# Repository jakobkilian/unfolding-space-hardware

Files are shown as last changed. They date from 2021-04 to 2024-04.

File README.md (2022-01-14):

# Unfolding Space Hardware

This repo contains the **hardware documentation of the “Unfolding Space” glove** – a prototypical open source navigation aid system for the visually impaired. 

Please check out the main repository of the [Unfolding Space](https://www.github.com/jakobkilian/unfolding-space) project for more information and a list of related repos anc content.

## Overall structure

In order to be able to use the Unfolding Space Glove, a relatively large amount of custom work is necessary. The following readme is only intended to give an overview of this and the contents of this repo. Note that not all details or design decisions are not documented here - if you really plan to build your own model, feel free to contact me if you have any questions.

The overall structure consists of 3 components:

- **5V USB power bank:** You can basically use any and wear it wherever you want. To keep the cable out of the way, I attached it to the upper arm with a sports arm band. I was using:
  - [Hama Power Pack *Supreme 10HD*](https://hama.com/00188307/hama-power-pack-supreme-10hd-10000mah). Raspis are picky about the supply voltage – if it drops too low (I think below 4.8 V), they reboot. Since they consume up to 3 A, the voltage of many batteries can easily drop below 5.0 V at peaks. Use high-quality power packs and 10 Ah to avoid this in advance or find one having stable output with > 4.9 V.
  - [SP Connect Running Band](https://sp-connect.com/collections/mounts/products/running-band) and a adhesive [Universal Interface](https://sp-connect.com/collections/phone-cases/products/universal-interface) was used to mount the power bank to the upper arm. Expensive but very reliable for this use case. There is tons of other, cheaper options out there.
- **USB-C Cable:** Here too, maintaining the voltage is crucial: use the shortest possible cable with good quality. The thickness of the insulation is a good indicator for low voltage drop, but only cutting and testing the copper wires can provide certainty. I had a 30 cm USB-A to USB-C cable from *Renkforce* in use (pictured), there may be plenty of others in your country.
- An finally **a) The Glove** hosting vibration motors and **b) the Unfolding Space Carrier Board** hosting the Raspberry Pi. See next sections.

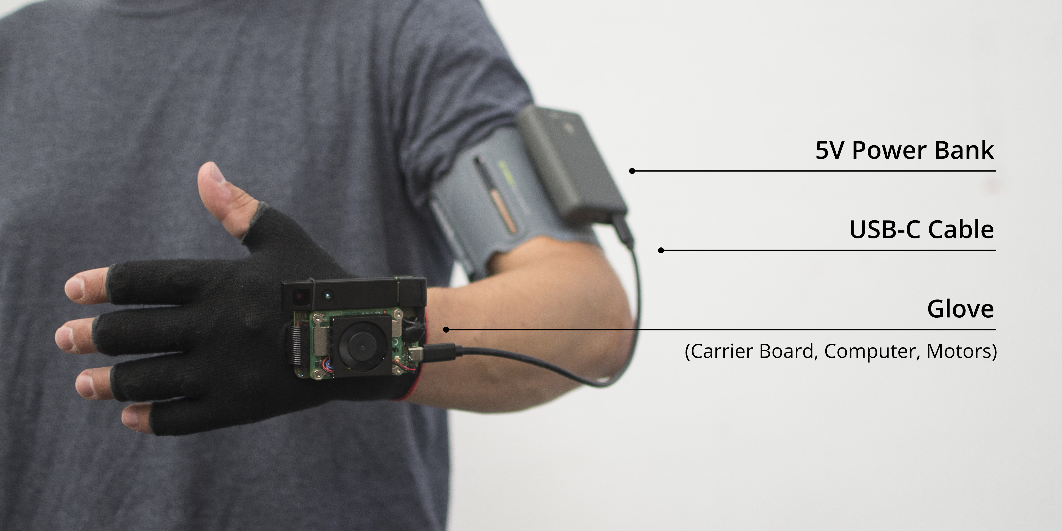
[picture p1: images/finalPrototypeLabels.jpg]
Prototype with labels


### a) The Glove

The glove consists of two textile layers between which the motors are attached and the cables are laid. On the outside (back of the hand) there are Velcro fasteners and an IDC connector for attaching the carrier board. Currently there are two sizes, fitting most hand shapes and sizes. The production of the glove is relatively elaborate and is explained step by step in the [glove](glove) directory of this repo.

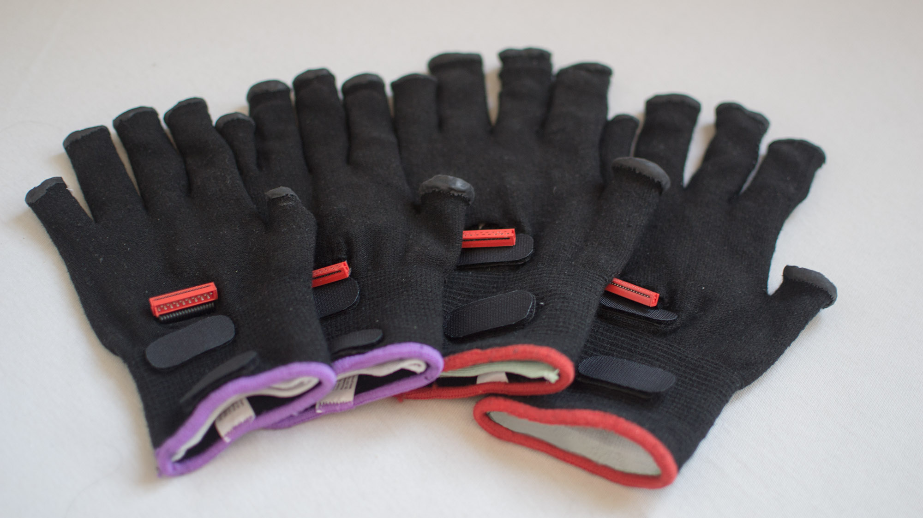
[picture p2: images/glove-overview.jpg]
Glove Overview


### b) Unfolding Space Carrier Board

The carrier board again consists of multiple components:

- The **Glove Connector** is implemented via an IDC connector soldered onto the PCB. *See [pcb](pcb)  directory for details and instructions.*
- The **ToF Camera** (a [Pico Flexx](https://pmdtec.com/picofamily/) camera from pmdtechnologies) is attached with a rubber band and a USB 3.0 Micro-B connector (originally this was a short cable), which is glued to the PCB. *See [pcb](pcb)  directory for details and instructions.*
- The **Raspberry Pi Compute Module 4** ([Link](https://www.raspberrypi.com/products/compute-module-4)) which serves as a computing unit. I used the CM4101016 configuration (16 GB Flash, 1 GB RAM, Wifi), a cheaper one (if available) would also do it as the app doesnt need much RAM.
- A **Cooling Fan for the CM4** was necessary because it became uncomfortably hot on warm days and passive cooling alone was not sufficient. At 24°C room temperature, the core temperature rose to >75°C without cooling, to ~67° with a small heat sink ([link](https://www.waveshare.com/cm4-heatsink.htm)) and to ~59°C with a larger one ([link](https://geekworm.com/products/cm4-12mm-aluminum-alloy-heatsink-c235?variant=33569307394136)). If you add a cooler to the latter ([link](https://geekworm.com/products/cm4-12mm-aluminum-alloy-heatsink-c235?variant=33569307426904)) or use [this smaller fan](https://www.waveshare.com/cm4-fan-3007.htm) (pictured) , it stays below 45°C. The last fan from Waveshare used in the picture operates with 12V and PWM. However, I used it without PWM and with 5V, which made it run very quietly.
- And then there is the **custom made PCB ** that carries the CM4 with two 100-pin mezzanine connectors, hosts the motors drivers, some electronics (gyro, compass, ...), the 5V USB-C power supply plug, the IDC connector to the glove and the USB connector to the ToF camera. ***See [pcb](pcb) directory for details and instructions.***

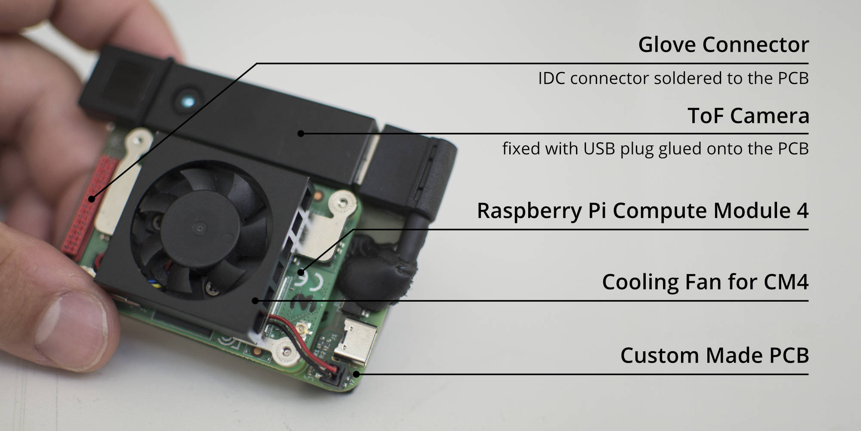
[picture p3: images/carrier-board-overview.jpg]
Carrier Board Overview


## Parts and Prices

There is a parts list / BOM with all components assembled on the root directory (called [bom-overall](bom-overall.csv)) which refers to further BOMs in directories [pcb](pcb) and [glove](glove). The total price of the overall structure is about $ 500, two thirds of which go to the ToF camera. Take a look at the BOMS for details.

## 3D Design

I did some 3D designs to check wheter the parts will fit and to dtermine size of the board etc. You can find them under [3D-design](3D-design), but note that they are not the final version (e.g. the cooling fan is not included) and they are for orientation only.

## Credits

Thanks to **[mattikra](https://github.com/mattikra)** and **[a2800276](https://github.com/a2800276)** from Press Every Key for helping me with the PCB design and ordering of the boards and parts!

Thanks to [dronecz](https://github.com/dronecz/Minimal_carrier_board_for_CM4)  and [timonsku](https://github.com/timonsku/Minimal-RPi-CM-4-Carrier) for some carrier board inspiration just after the CM4s were released.

Thanks to Shawn Hymel for providing a [tutorial on CM4 carrier boards](https://www.digikey.com/en/maker/projects/creating-a-raspberry-pi-compute-module-4-cm4-carrier-board-in-kicad/7812da347e5e409aa28d59ea2aaea490) and an exemplary KiCad template file (included in [pcb](pcb) , licensed under CC-BY-4.0)

Thanks to KiCad for providing Software and [Libraries](https://gitlab.com/kicad/libraries) for this project.

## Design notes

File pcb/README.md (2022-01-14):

# Custom PCB: Unfolding Space Carrier Board Rev. 2

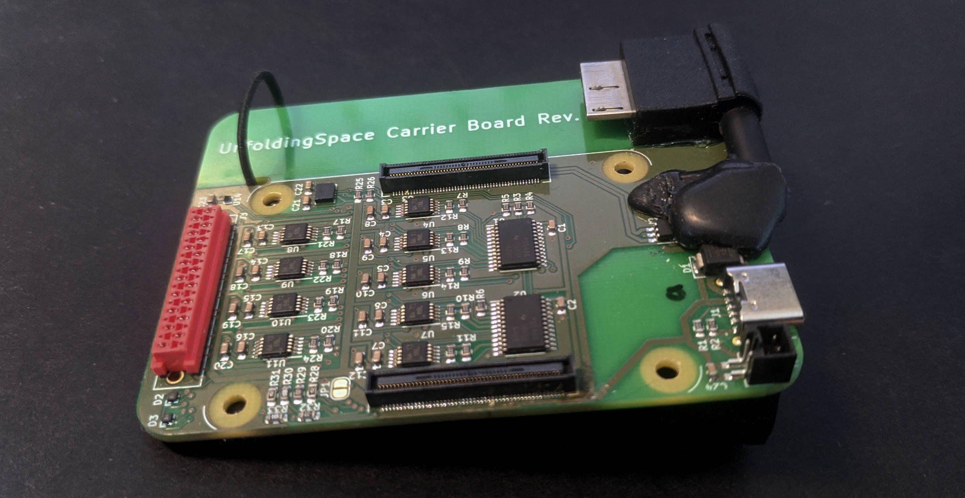
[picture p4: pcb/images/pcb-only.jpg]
The printed circuit board without Raspberry Pi and camera


## PCB Design Files

You can find the **design files** in [KiCad-Project-Rev2](KiCad-Project-Rev2) and exports (**schematic, pcb layout, rendering**) in [exports](exports).

**Design rules** are based on the specifications of a *2-layer, complex, ENIG* board at aisler.net. Note that some of my rules thus are a bit unusual (e.g. clearance ≥ 0.1 mm or track width ≥ 0.2 mm; through whole ≥ 0.3mm). [See all specifications of Aisler here.](https://aisler.net/help/design-rules-and-specifications/design-rules) 

There also is a [Aisler project of the Rev. 2 board online](https://aisler.net/p/WSTOTZAR) if you are from Europe. Attention: the BOM / parts list needs to be updated to respective components by hand!

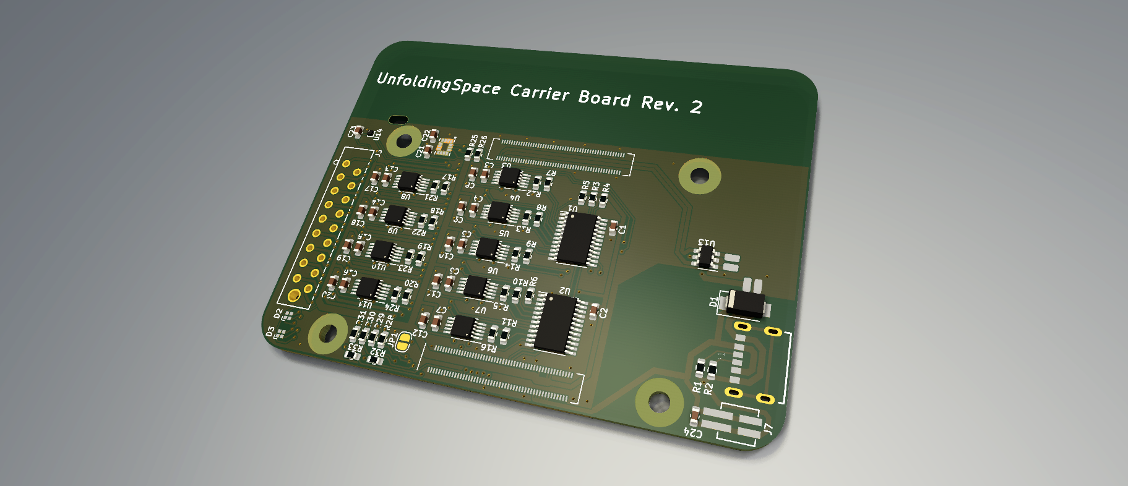
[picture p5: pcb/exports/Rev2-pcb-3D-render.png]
unfolding2


## BOM / parts list

See [bom-pcb](bom-pcb.csv) for a list with all needed parts for the pcb alone.

## Known issues

- Some parts (e.g. RGB LEDs, IMU and MMC) are very (very) small! We could successfully reflow them but it was quite a hustle.
- The RGB LEDs in the upper right corner are very bright in the current layout. We thus use GPIO pins of the raspi with pull-up resistor to drive them on lower light intensity. Consider changing the resistors on the board!
- The i2c multiplexer (PCA) is needed because the drv chips just have one i2c address. You could also use the drv2603 and use pwm to drive them. Writing on all 9 drvs with the multiplexer takes around 3ms. Not much time to save anyway...
- Shortly before dispatch, the pico-spox plug in the bottom left corner was added to drive a cooling fan with 5 V. Consider using a 4-pin plug and using pwm instead.

## Credits

Thanks to **[mattikra](https://github.com/mattikra)** and **[a2800276](https://github.com/a2800276)** from Press Every Key for helping me with the PCB design and ordering of the boards and parts!

Note the txt files in the directories of 3rd party assets for credits and licenses.

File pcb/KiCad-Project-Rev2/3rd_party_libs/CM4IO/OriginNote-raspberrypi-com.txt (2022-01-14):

Note that this library is taken from https://github.com/ShawnHymel/rpi-cm4-base-carrier, licensed under CC-BY-4.0. 

The CM4IO library is also availabe at https://www.raspberrypi.com/products/compute-module-4-io-board/

If you want to use the file(s) in your own project, consider downloading it yourself.

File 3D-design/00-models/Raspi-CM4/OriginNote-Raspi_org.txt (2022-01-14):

Note that this asset is taken from https://datasheets.raspberrypi.com

There it says:
_______________
All design files are made available openly, with no limitations. Files hosted on this site and under this licence include,
cm4/CM4-step.zip

Permission to use, copy, modify, and/or distribute this design for any purpose with or without fee is hereby granted.

THE DESIGN IS PROVIDED "AS IS" AND THE AUTHOR DISCLAIMS ALL WARRANTIES WITH REGARD TO THIS DESIGN INCLUDING ALL IMPLIED WARRANTIES OF MERCHANTABILITY AND FITNESS. IN NO EVENT SHALL THE AUTHOR BE LIABLE FOR ANY SPECIAL, DIRECT, INDIRECT, OR CONSEQUENTIAL DAMAGES OR ANY DAMAGES WHATSOEVER RESULTING FROM LOSS OF USE, DATA OR PROFITS, WHETHER IN AN ACTION OF CONTRACT, NEGLIGENCE OR OTHER TORTIOUS ACTION, ARISING OUT OF OR IN CONNECTION WITH THE USE OR PERFORMANCE OF THIS DESIGN.

The models provided in the 3dmodels directory as part of the CM4 design files are from various manufacturers including; Diodes, MTCONN, Toby, TRXCOM. Terms and conditions for the use of the models remain with the original manufacture.

also see: https://datasheets.raspberrypi.com/licence.html

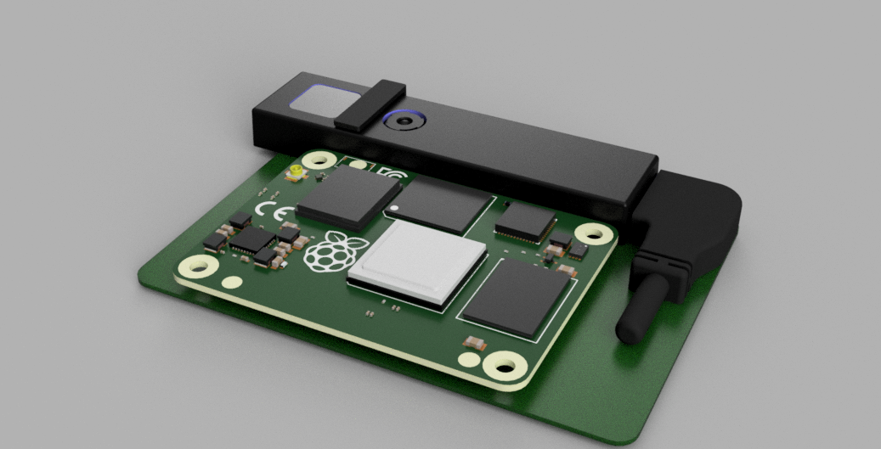
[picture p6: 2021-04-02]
3D-design/02-exports/210402_export.png

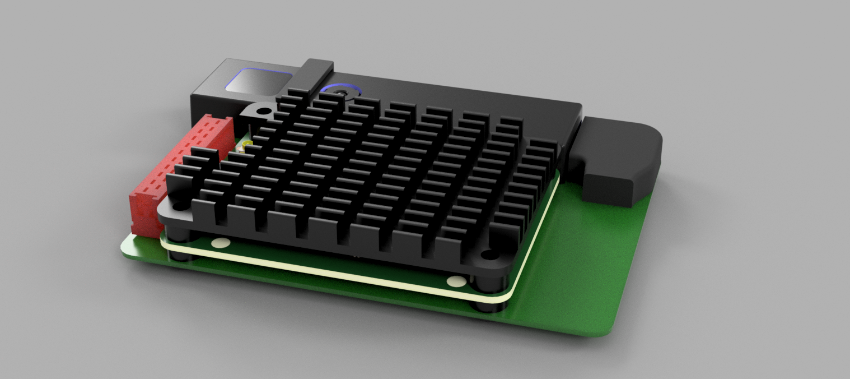
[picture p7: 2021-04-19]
3D-design/02-exports/200412_export_2.png

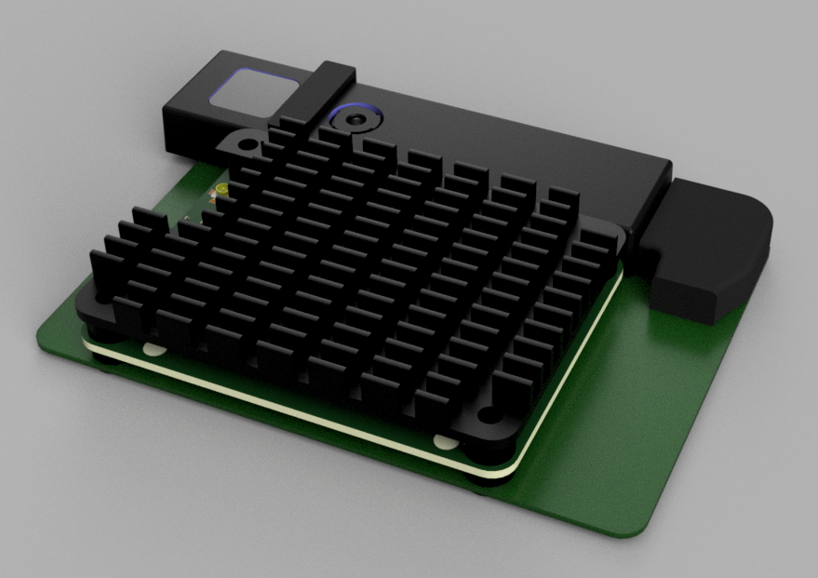
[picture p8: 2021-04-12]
3D-design/02-exports/210412_export.png

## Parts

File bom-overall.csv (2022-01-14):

Id | Designator | Manufacturer | Quantity | Designation | Description | Est. Price EUR | Link
1 | pcb |  | 1 |  | see pcb bom for details | 66 | pcb/bom-pcb.csv
2 | glove |  | 1 |  | see glove bom for details | 47 | glove/bom-glove.csv
3 | Raspberry Pi Compute Module 4 | Raspberry Pi Foundation | 1 | CM4101016 | CM4101008 would also suffice | 40
 | Cooling Fan for the CM4 | Waveshare | 1 | cm4-fan-3007 |  | 9 | https://www.waveshare.com/cm4-fan-3007.htm
 | ToF Camera | pmdtechnologies ag | 1 | CamBoard Pico Flexx | version 2 released in Jan 2022 | 300 | https://www.automation24.co.uk/development-kit-pmd-vision-r-camboard-pico-flexx-700-000-094
 | USB-C Cable | Renkforce | 1 | RF-3241262 | short USB-C cablecould be anyÉ | 7
 | 5V USB power bank | Hama | 1 | 188307 | 10 Ah Power Bank, could be anyÉ | 20
 |  |  |  |  | SUM | 489

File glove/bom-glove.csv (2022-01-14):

Id | Designator | Manufacturer | Quantity | Designation | Description | Est. Price EUR | Link
s | inner glove layer | Munitec GmbH | 1 | 12025 | clean room glove made of polyamide | 1 | https://www.munitec-gmbh.de/polyamid-reinraum-handschuhe-glatt.html
2 | outer glove layer | Worksave | 1 | L71-720 | see glove bom for details | 1
3 | sock stop liquid latex |  | 1 |  | Available in any craft shop or online | 2
4 | wooden stick 19mm |  | 1 |  | Available in any craft shop or online | 1
5 | Flat ribbon cable | 3M | 1 | 8125/10 100 | grey cable, found a black one in a local shop | 2 | https://www.digikey.de/short/fwfd03w9
6 | IDC Connector | TE Connectivity | 1 | 8-215083-8 | idc connector to join pcb and glove | 7 | https://www.digikey.de/short/3zfqqqv3
7 | Vibration Motors | Jinlong Machinery & Electronics | 1 | G1040003D | Strong LRA vibration motors. They seem to have changed their Designation to: VG1040003D Ð Vybronics, Inc | 29 | https://www.digikey.de/short/zwzpjh5d
8 | heat shrink tube |  | 1 |  | availbe in any electronics store or online | 1
9 | velcros |  | 4 |  | Available in any craft shop or online | 2
10 | motor adhesive surface | 3M | 1 | 3M241471 | needed to glue textile and shrink tube | 1 | https://www.3m.co.uk/3M/en_GB/p/d/v000090527/
 |  |  |  |  | SUM | 47

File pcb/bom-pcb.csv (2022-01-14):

Id | Designator | Package | Quantity | Designation | Description | Est. Price EUR | Link
1 | J3 | https://www.digikey.de/de/products/detail/te-connectivity-amp-connectors/8-215083-8/1955684 | 1 | 1-338068-8 | IDC socket for glove connection | 1.5
2 | C19;C15;C10;C13;C9;C5;C16;C14;C12;C24;C4;C2;C1;C3;C8;C20;C17;C18;C11;C6;C7 | C_0603_1608Metric | 21 | 1u | capacitor | 1
3 | C21;C22 | C_0603_1608Metric | 2 | 100n | capacitor | 0
4 | C23 | C_0603_1608Metric | 1 | 2.2u | capacitor | 0
5 | D1 | D_SMA | 1 | SMBJ5.0A | ESD for USB-C power supply | 0.5
6 | J1 | GCT_USB4125-GF-A_REVA | 1 | USB4125-GF-A_REVA | USB-C power supply socket | 0.5
7 | ToFCam-Stecker | Micro-USB30-Plug | 1 | System-S USB 3.0 cable | glued USB plug | 9 | https://www.system-s.com/USB-3-0-Micro-B/SYSTEM-S-Micro-USB-3-0-Kabel-90-GRAD-Grad-Winkel-Rechts-gewinkelt-auf-USB-Typ-A-3-0-Aufwaerts-gewinkelt-Adapter-Daten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
8 | J7 | PICOspox-2-v | 1 | PICOspox-2-v | cooling fan plug | 0.5
9 | U12 | PQFN50P250X300X100-14N | 1 | LSM6DSxx | IMU / Accelerometer and Gyroscope | 5
10 | R28;R31 | R_0603_1608Metric | 2 | 1K | resistor | 0
11 | R18;R19;R17;R7;R11;R13;R16;R3;R20;R9;R22;R26;R15;R24;R10;R25;R12;R4;R23;R8;R14;R21 | R_0603_1608Metric | 22 | 2K2 | resistor | 1
12 | R29;R32 | R_0603_1608Metric | 2 | 220 | resistor | 0
13 | R33;R30 | R_0603_1608Metric | 2 | 150 | resistor | 0
14 | R6;R5 | R_0603_1608Metric | 2 | 10K | resistor | 0
15 | R1;R2 | R_0603_1608Metric | 2 | 5K1 | resistor | 0
19 | U13 | SOT-23-6 | 1 | WE 82400102 | TVS diode for USB data (camera) | 1
20 | U2;U1 | TSSOP-24_4.4x7.8mm_P0.65mm | 2 | TCA9548APWR | i2c multiplexer | 7
21 | D3;D2 | UHD1110-FKA | 2 | UHD1110-FKA | RGB LED | 0.5
22 | U3;U5;U10;U8;U4;U11;U9;U7;U6 | VSSOP-10_3x3mm_P0.5mm | 9 | DRV2605LDGS | motor driver | 33
23 | U14 | WLP-4_0.86x0.86mm_P0.4mm | 1 | MMC5633NJL | compass | 1.5
24 | - |  | 2 | DF40HC(3.0)-100DS-0.4V(51 | 100pin mezzanine connector for CM4 | 4 | https://www.mouser.de/ProductDetail/Hirose-Connector/DF40HC30-100DS-04V51?qs=%252BAZVS4b%2FkgIV%252B3vHYy2dCA%3D%3D
25 | - |  | 1 |  | Board production | 10
 |  |  |  |  | SUM | 76

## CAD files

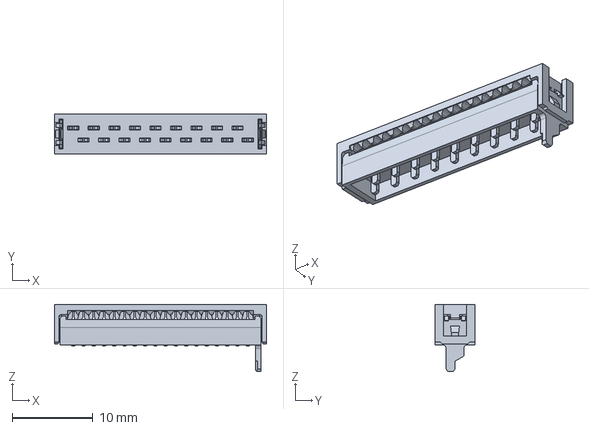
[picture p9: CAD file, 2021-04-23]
3D-design/00-models/TE-Connectors/c-1-215083-8-u-3d.stp
26.2 x 5.00 x 8.35 mm

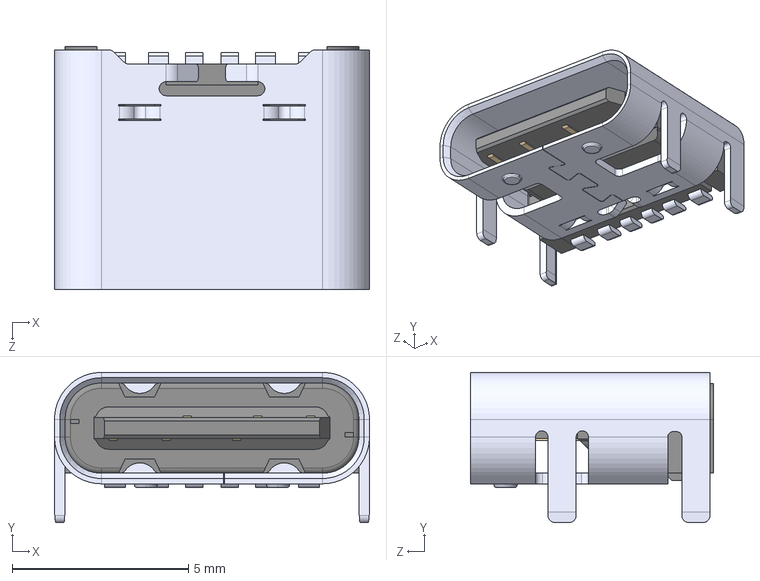
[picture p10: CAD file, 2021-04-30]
pcb/KiCad-Project-Rev2/3rd_party_libs/UJC-HP-3-SMT-TR/UJC-HP-3-SMT-TR.step
8.94 x 4.26 x 6.90 mm

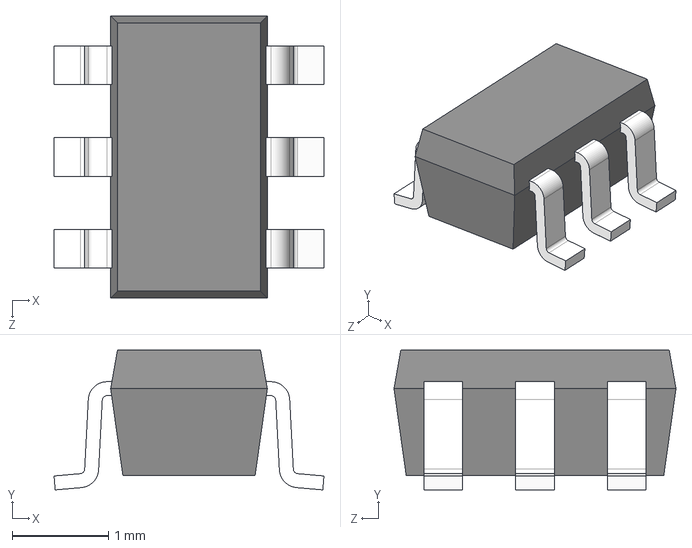
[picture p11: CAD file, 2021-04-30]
pcb/KiCad-Project-Rev2/3rd_party_libs/USBLC6-2SC6/USBLC6-2SC6.step
2.80 x 1.45 x 2.92 mm

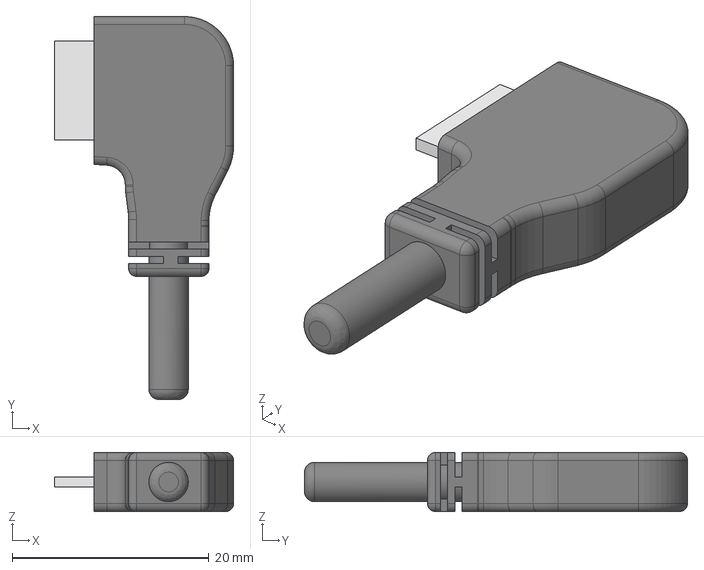
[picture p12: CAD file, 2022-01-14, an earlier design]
3D-design/00-models/USB-plug-deprecated/startech-plug.step
18.2 x 38.9 x 6.00 mm

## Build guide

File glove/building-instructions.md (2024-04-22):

# Building the Glove

This is a building instruction for the glove needed to build the the [Unfolding Space Glove](https://github.com/jakobkilian/unfolding-space).

## Overview

The glove has two layers of fabric with the vibration motors and cables in between. There is velcro to attach the Unfolding Space Carrier Board (see pcb directory of this repo) to it and a ribbon cable exiting the back of the glove terminating with an idc connector to link glove and board. The end result looks like this (two sizes: red = big and purple = small): 

The glove when it is finished. There are two sizes: red = big and purple = small

## 1. Textile Work

First of all, we need the inner and outer layers of the glove. You could sew these yourself, but this is very time-consuming. I therefore looked for suitable models which I could work with. It quickly became clear that both gloves had to be very thin, because otherwise the construction would be too thick and uncomfortable. In order to achieve a high degree of stretch and durability at the same time, I looked primarily for polyamide textiles. Most of them are work gloves with coating, which made the search more difficult.

I found what I was looking for in a very thin inner layer of a polyamide [clean room glove ](https://www.munitec-gmbh.de/polyamid-reinraum-handschuhe-glatt.html)(article number 12025) from Munitec (they were kind enough to provide me with samples of their collection). They can also be cut well without becoming frayed.

The outer layer should meet basic aesthetic requirements, look neutral and also be stretchable and resistant. Here it was a no name (Worksafe L71-720) product from Amazon (though I hate buying there).

### Outer Layer

I cut the fingers of the gloves halfway so that the two sizes would fit as well as possible on different hands. 

| Cut the Fingers Halfway                                                                                              |
|:--------------------------------------------------------------------------------------------------------------------:|
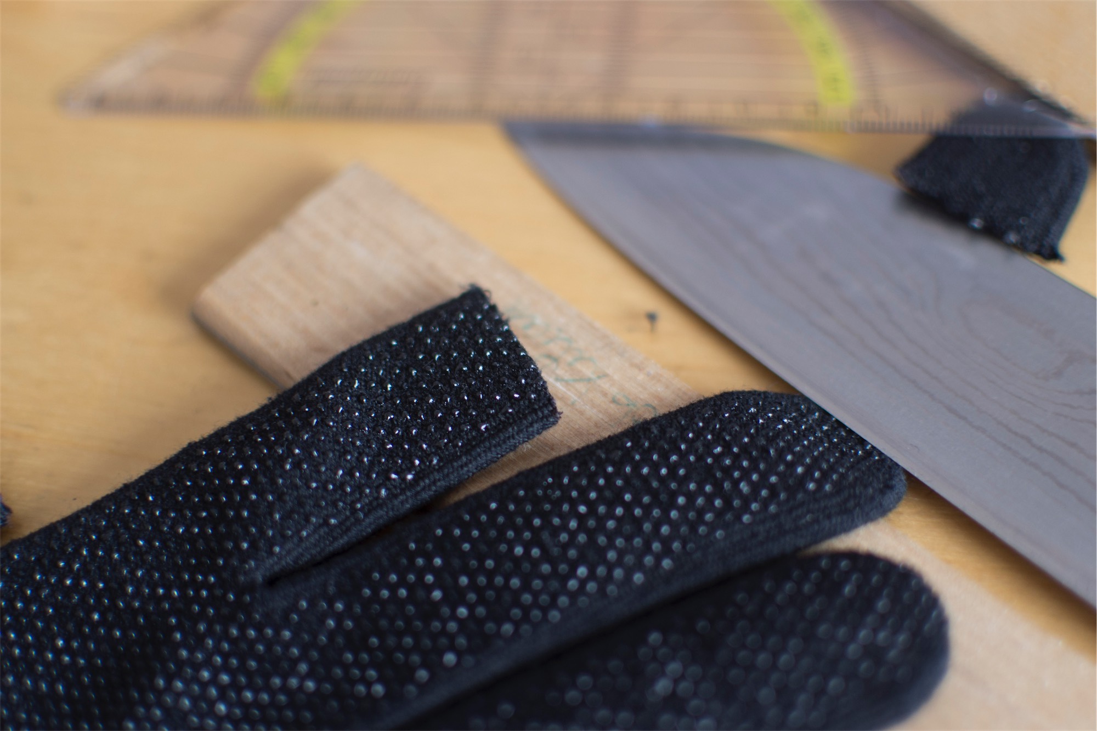
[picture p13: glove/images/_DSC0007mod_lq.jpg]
A kitchen knife next to the cut-in-half finger of the black glove on a wooden surface.
|  |
| To avoid fraying in the first place, it proved most effective to use a sharp kitchen knife                           |

Since I don't have a tool to hem the cut edges of the fingers (no idea how that would work), I experimented a bit with anti-fraying glue and the like and finally settled on liquid latex, typically used to make anti-slip socks. With some wooden stuffing of the fingers I was able to dip them into the latex and cut a clean edge after drying:

| Stuffing Material                                                                       | Just Before Dipping                                                                                                 |
|:---------------------------------------------------------------------------------------:|:-------------------------------------------------------------------------------------------------------------------:|
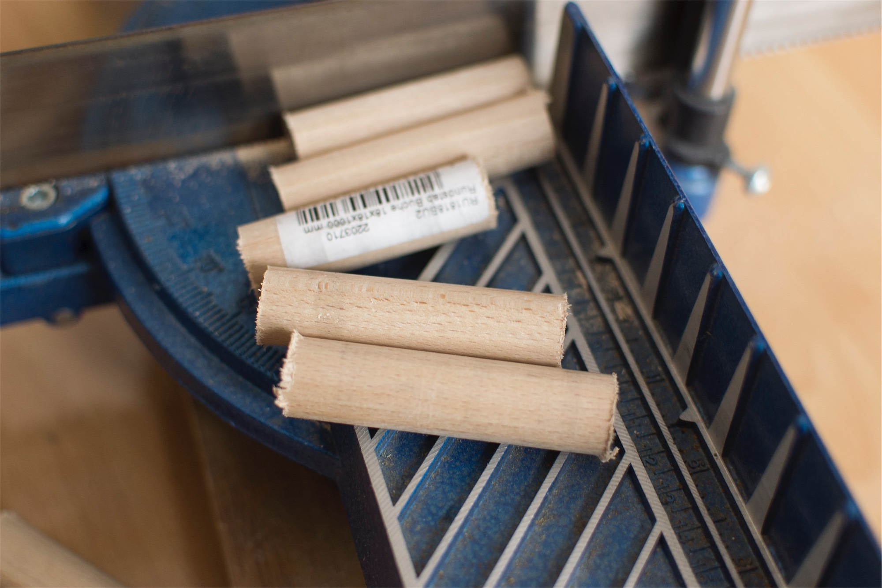
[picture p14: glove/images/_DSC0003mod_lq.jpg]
Short pieces of a wooden stick used as stuffing material.
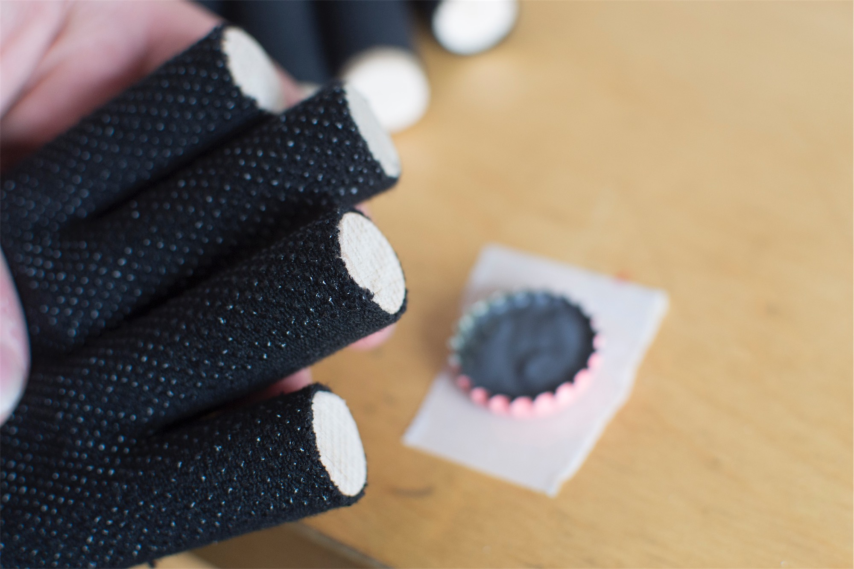
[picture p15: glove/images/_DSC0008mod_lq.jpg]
The fingers of the glove stuffed with the pieces of wooden stick just before dipping.
|  |  |

| After Dipping                                                                                           | Drying...                                                                          |
|:-------------------------------------------------------------------------------------------------------:|:----------------------------------------------------------------------------------:|
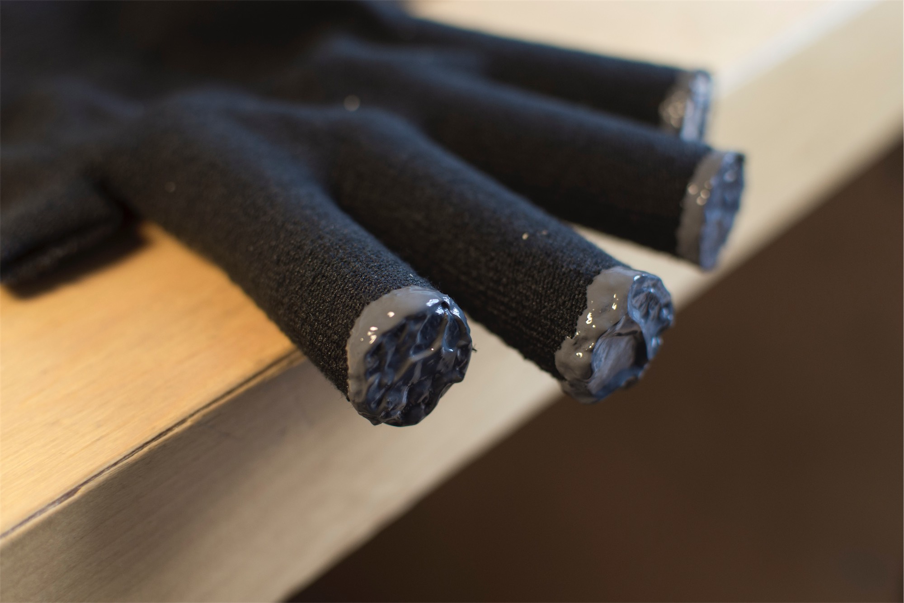
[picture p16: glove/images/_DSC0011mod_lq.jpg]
Fresh, grey liquid latex at the fingertips of the glove after dipping it.
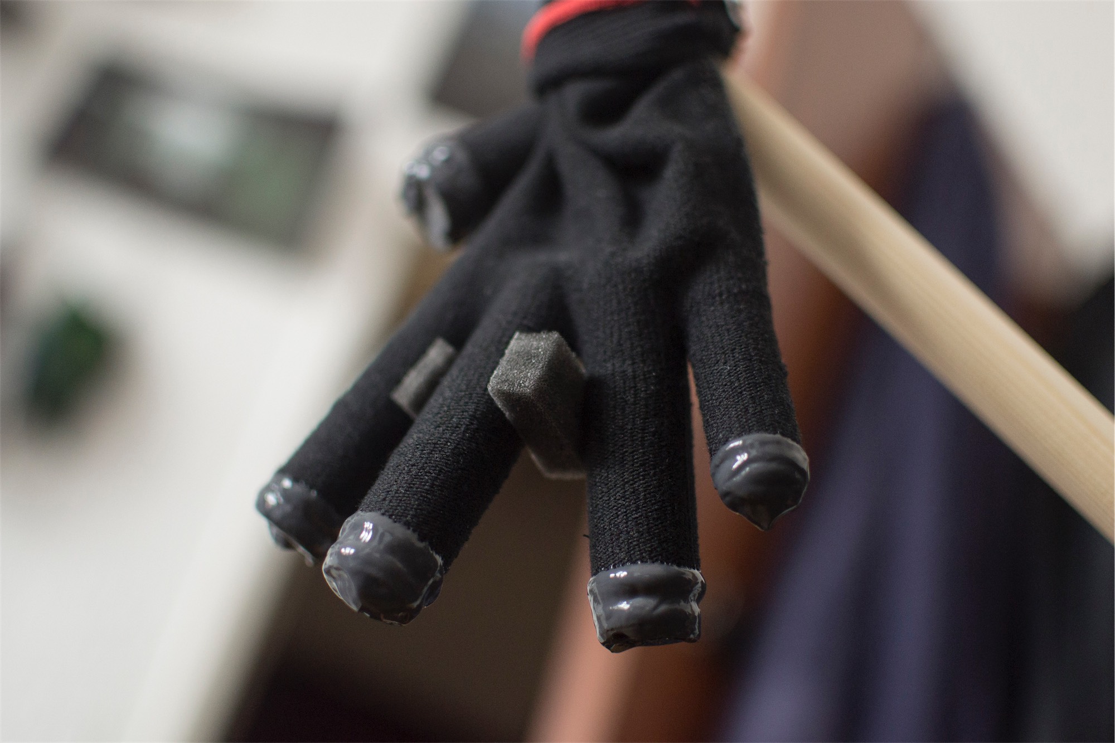
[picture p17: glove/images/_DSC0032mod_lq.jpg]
Suspended glove with drying latex on the fingertips.
|  |  |

| Getting Rid of Overhang                                                       | Finish Edges                                                                                                                |
|:-----------------------------------------------------------------------------:|:---------------------------------------------------------------------------------------------------------------------------:|
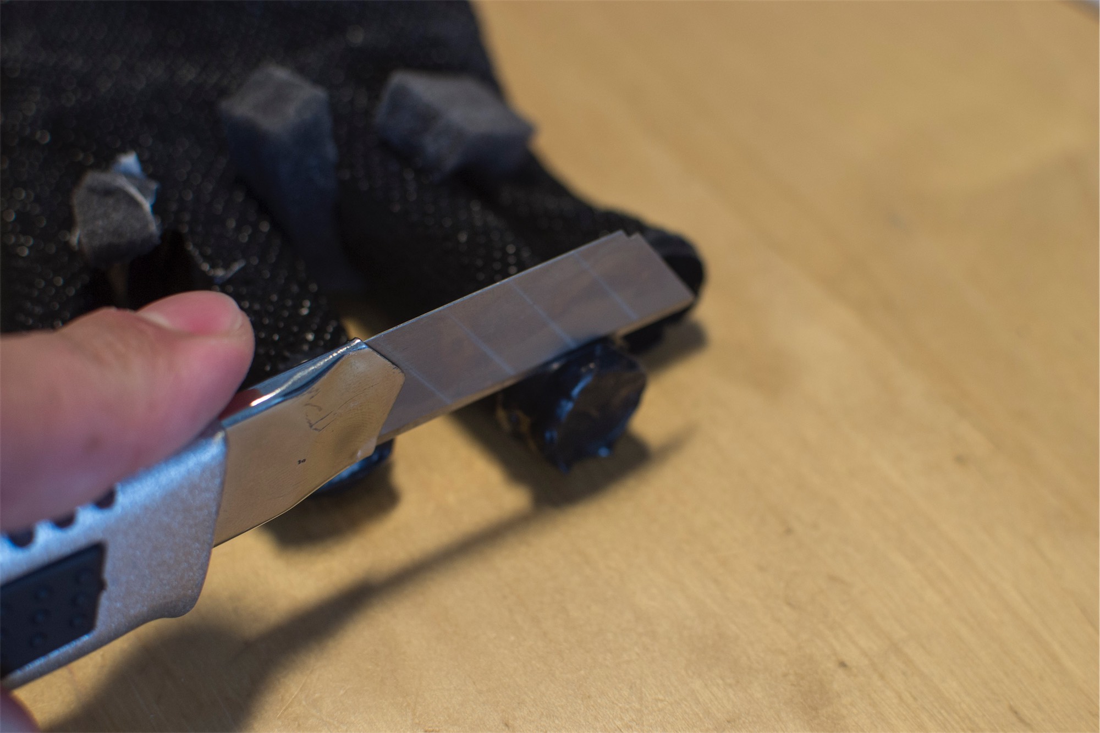
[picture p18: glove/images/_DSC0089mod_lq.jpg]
A cutter cuts away the overhanging latex lumps.
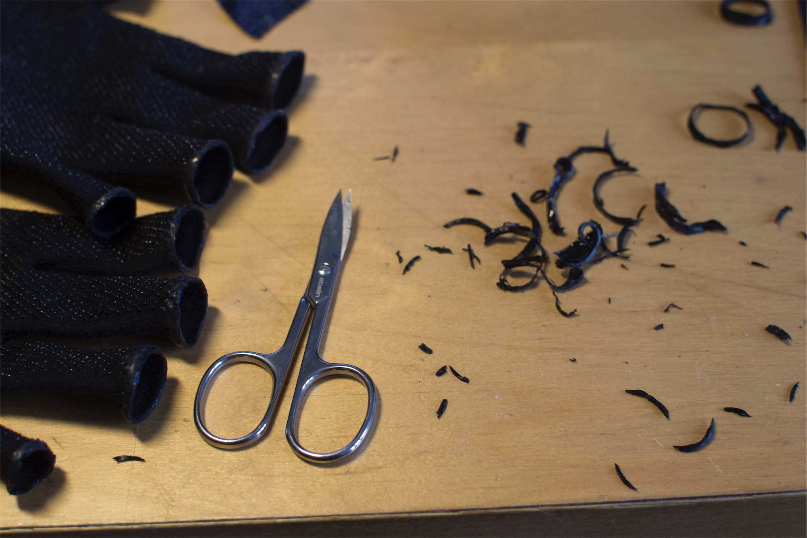
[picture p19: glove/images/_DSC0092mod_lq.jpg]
A small pair of scissors lies on the table next to the glove. Fine cuttings lie next to them.
|  |  |

Resulting in these edges that do their job of not fraying and not looking too bad:

| Result                                                                                                         |
|:--------------------------------------------------------------------------------------------------------------:|
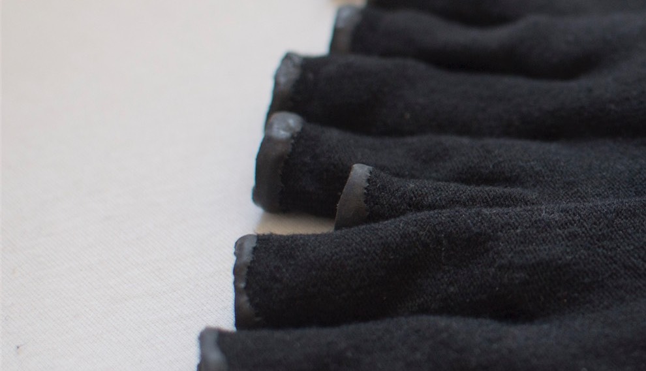
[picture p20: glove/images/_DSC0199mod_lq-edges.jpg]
Macro shot of several gloves with focus on the finished, hemmed fingertips
|  |

## Inner Layer

Next I determined the position of the motors so that they are equally spread over the available surface and do not interfere with hand movements. 

| Positioning of the Motors                                                                                                                             | Reproducing Inner Layers                                                                                            |
|:-----------------------------------------------------------------------------------------------------------------------------------------------------:|:-------------------------------------------------------------------------------------------------------------------:|
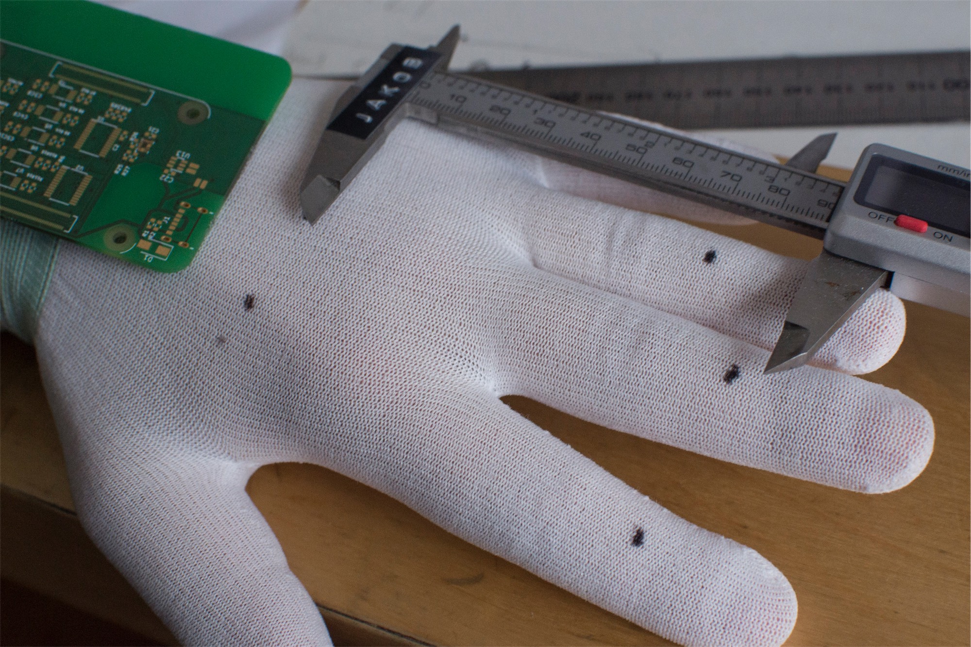
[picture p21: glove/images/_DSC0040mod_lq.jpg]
A sliding gauge and the thin, white, inner glove layer on which points can be seen where the motors are to be attached.
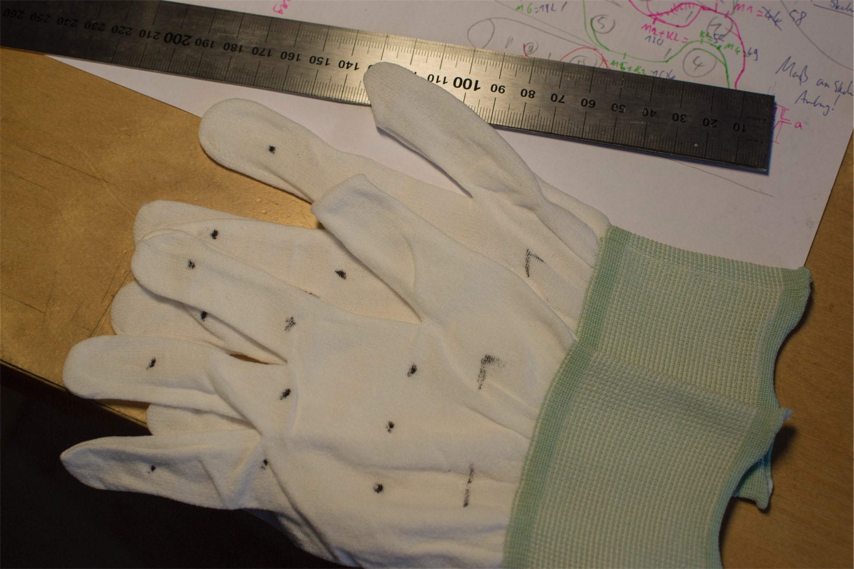
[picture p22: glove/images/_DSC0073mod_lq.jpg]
Two of the inner layer gloves with the same markings for motors, board and the like.
|  |  |

The inner gloves were cut in the same way as the outer ones but with slightly longer fingers so that they could be folded over and sewn by hand to the outer glove (no picture).

## 2. Preparing the Motors and Cables

Regarding the motors experience from older prototypes revealed two particular weaknesses that can occur when there is a lot of physical stress: 

- The **breaking of the solder joints** on the vibration motor's solder pad.
- The **tearing of cables from the connector** on the other side due to excessive tensile stress. These occur due to the great mobility of the hands.

To prevent **breaking of the solder joints**, I soldered the cables onto the soldering pad so that they ran past the motor to the rear. If you then wrap the entire motor in a heat-shrink tube, the soldering point is relieved of strain in a cost-effective way and the problem is solved. 

| Soldering of the cables                                                                          |
|:------------------------------------------------------------------------------------------------:|
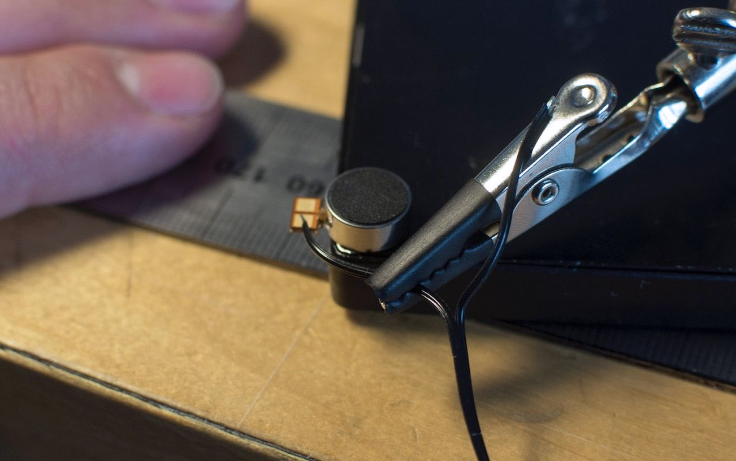
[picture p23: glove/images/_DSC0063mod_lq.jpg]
An affixed vibration motor which just gets a lead end soldered on.
|  |

| Add Heat Shrink Tubing                                                                                                                        | Shrink Them                                                                               |
|:---------------------------------------------------------------------------------------------------------------------------------------------:|:-----------------------------------------------------------------------------------------:|
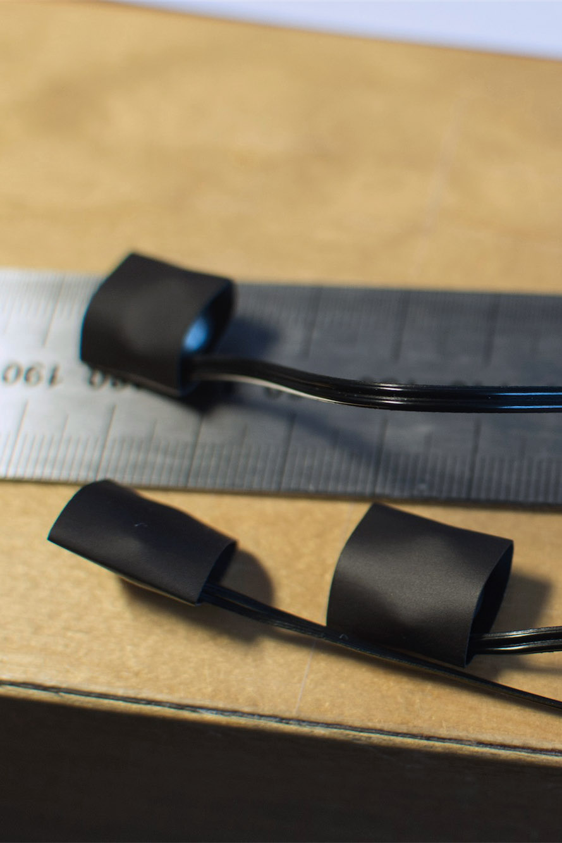
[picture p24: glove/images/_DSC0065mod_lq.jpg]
A heat shrink tubing around three motors, the cables coming out of them on the opposite side of the solder pad.
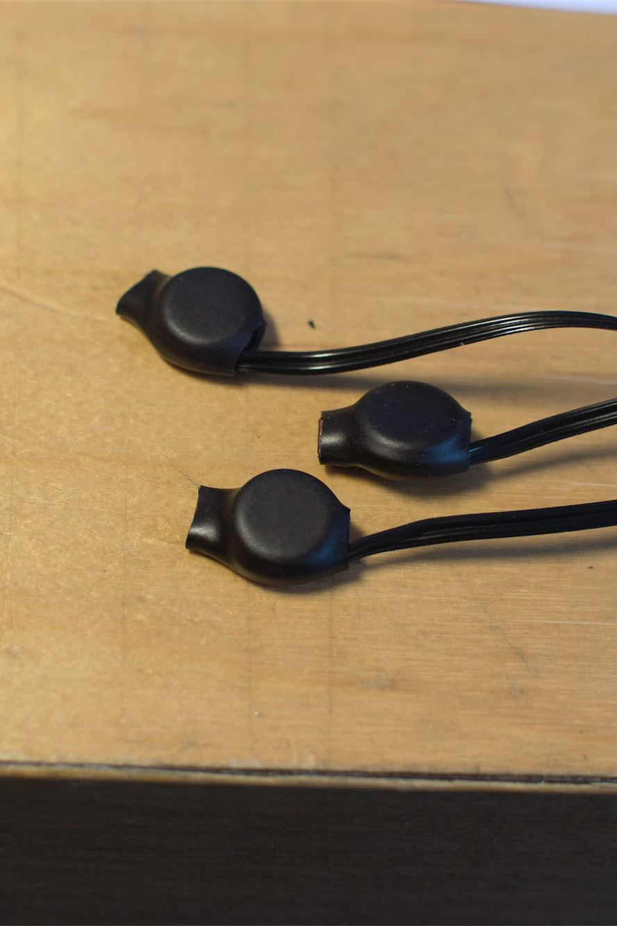
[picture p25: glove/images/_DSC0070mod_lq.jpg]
The tubing shrunk tightly around the motors and the cables.
|  |  |

| Before and After                                                                                        |
|:-------------------------------------------------------------------------------------------------------:|
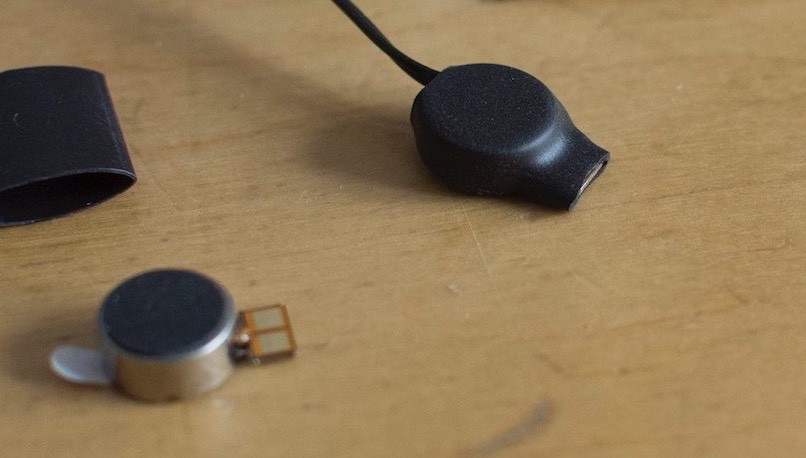
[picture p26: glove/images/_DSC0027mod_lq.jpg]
A bare motor without cables and the soldered, and shrunk version besides.
|  |

Next to prevent **tearing of cables from the connector** I tried to route the cables in a meandering way on the inner layer of the glove so that they bypass all the joints of the hand that can cause tension on the cable.

| Routing Experiments                                                                                                                  |
|:------------------------------------------------------------------------------------------------------------------------------------:|
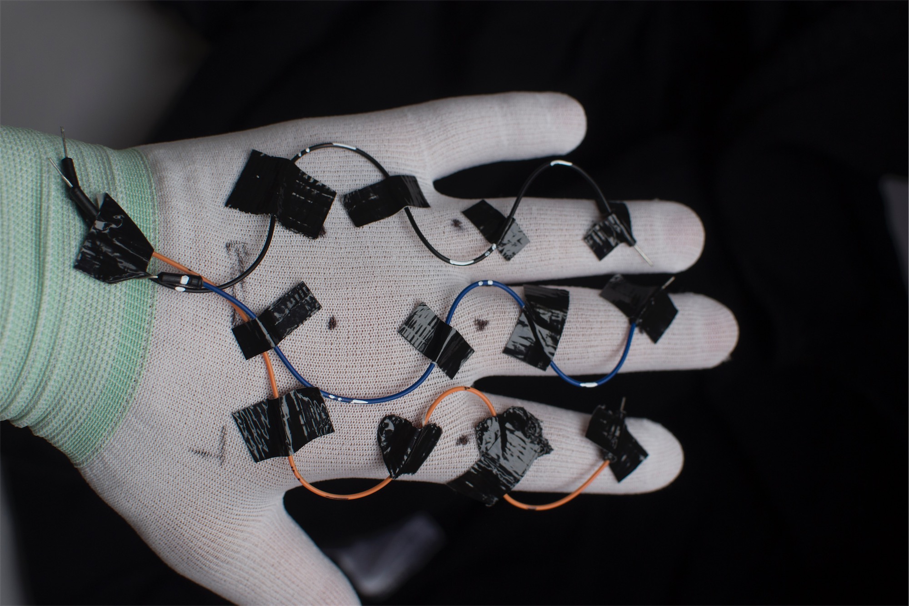
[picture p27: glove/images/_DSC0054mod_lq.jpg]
The thin, white, inner textile layer with short cables taped on it to demonstrate a possible routing
|    |
| With this routing, the cable is not heavily stressed by any the movement of the hand. The dots represent the position of the motors. |

| Testing the Cable Exit Point                                                                                                                         |
|:----------------------------------------------------------------------------------------------------------------------------------------------------:|
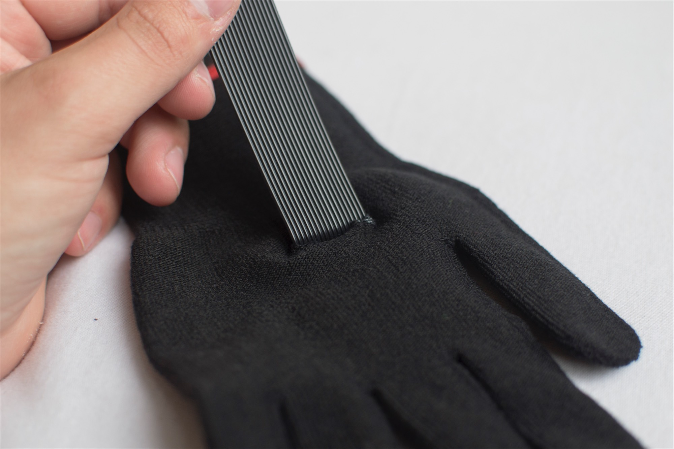
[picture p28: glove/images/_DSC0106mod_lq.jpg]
A flat ribbon cable exiting the outer, black layer of the glove at its back through a cutted slot to test the routing.
|  |
| Testing the exit point of the flat ribbon cable that is used in the final setup.                                                                     |

## 3. Implementation of the Wiring

With the routing being determined, I could produce the wiring strands using flat ribbon cables:

| Cutting, Soldering, Wrapping                                                                                          | Apply Adhesives to Motors                                                                                |
|:---------------------------------------------------------------------------------------------------------------------:|:--------------------------------------------------------------------------------------------------------:|
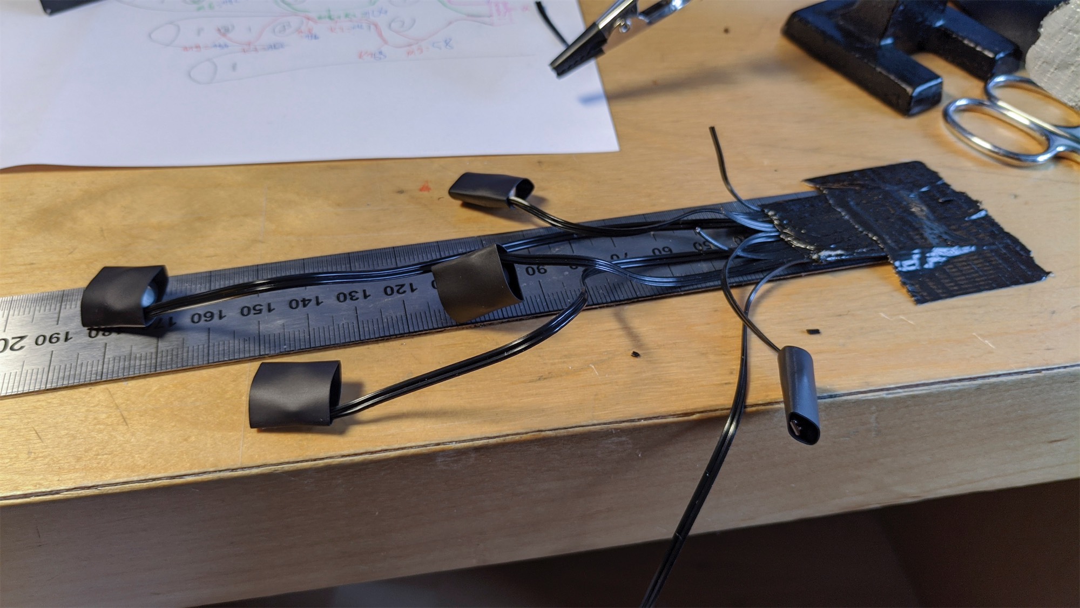
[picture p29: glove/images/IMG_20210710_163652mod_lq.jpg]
A flat ribbon cable with the motors soldered to the wires placed on a ruler.
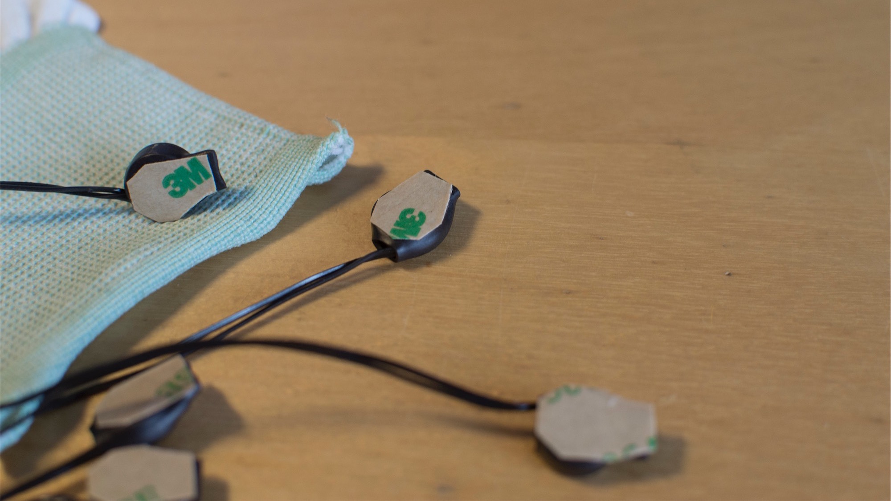
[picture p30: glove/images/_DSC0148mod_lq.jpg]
The finished motors in shrink tubing with adhesive surfaces on the bottom.
|  |  |

| Crimping the IDC Connector & Testing Connections                                                |
|:-----------------------------------------------------------------------------------------------:|
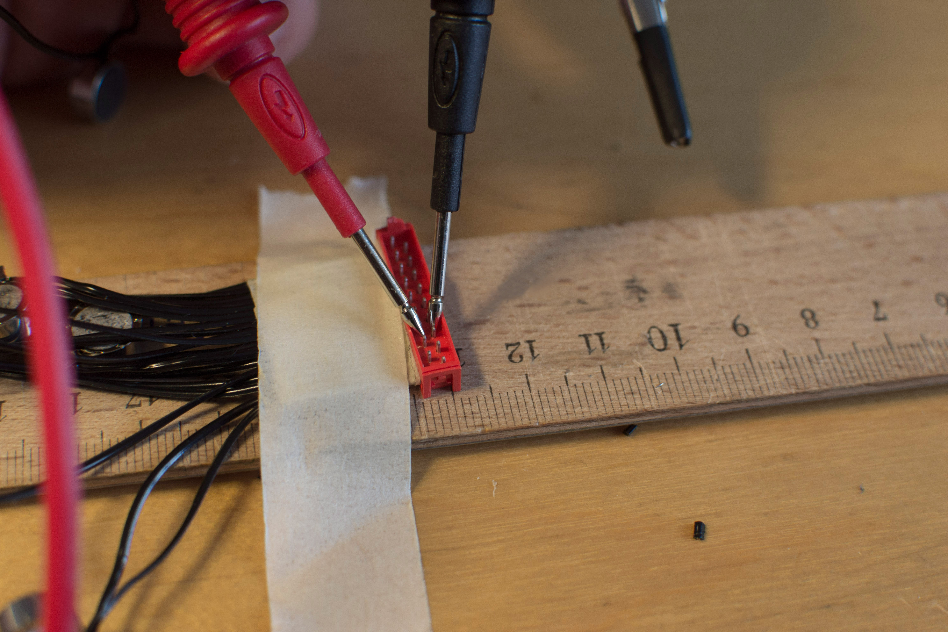
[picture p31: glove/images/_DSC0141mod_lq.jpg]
|  |

| Resulting Wiring Glued onto the Glove                                                           |
|:-----------------------------------------------------------------------------------------------:|
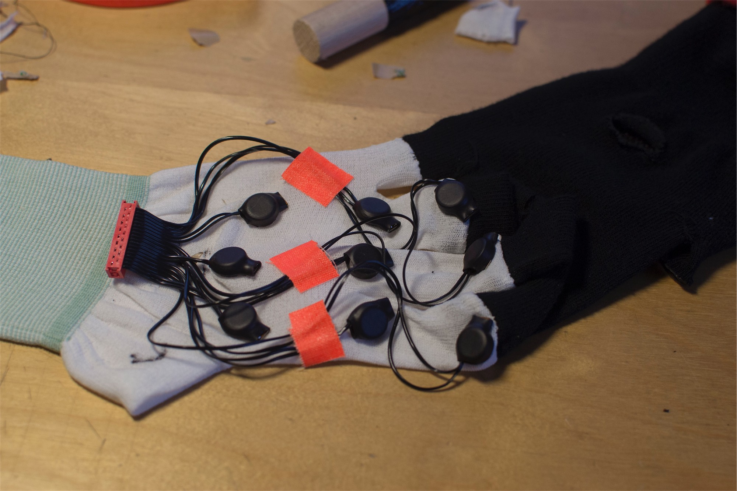
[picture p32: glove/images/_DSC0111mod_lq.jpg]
|  |

## 4. Sewing of the Cables

The cables then had to be sewed onto the glove by hand. For this I used a cardboard hand from the craft shop that. 

| Sewing                                                                                                                                   |
|:----------------------------------------------------------------------------------------------------------------------------------------:|
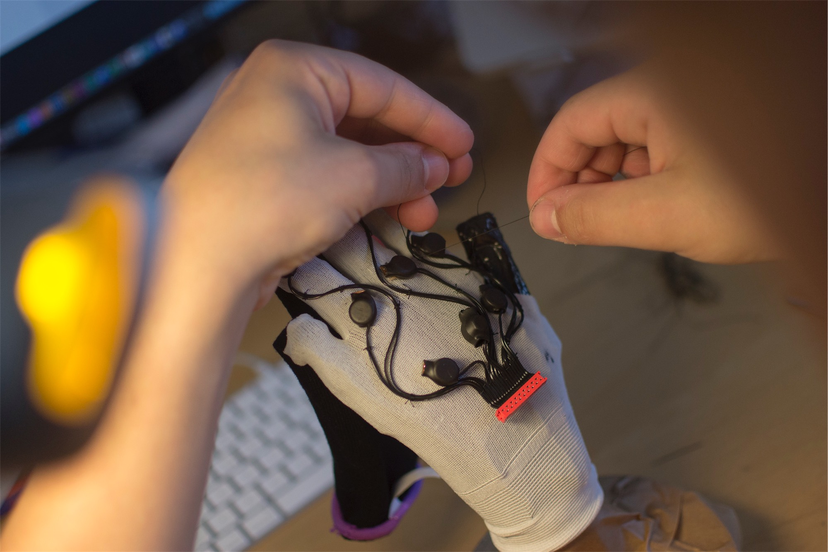
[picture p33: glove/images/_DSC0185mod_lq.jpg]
The glove affixed on the carboard hand and in bright lighting condition gets sewed with needle and thread.
|  |
| The quite time consuming process of sewing all cables onto the inner textile layer                                                       |

| Result                                                                                                                       |
|:----------------------------------------------------------------------------------------------------------------------------:|
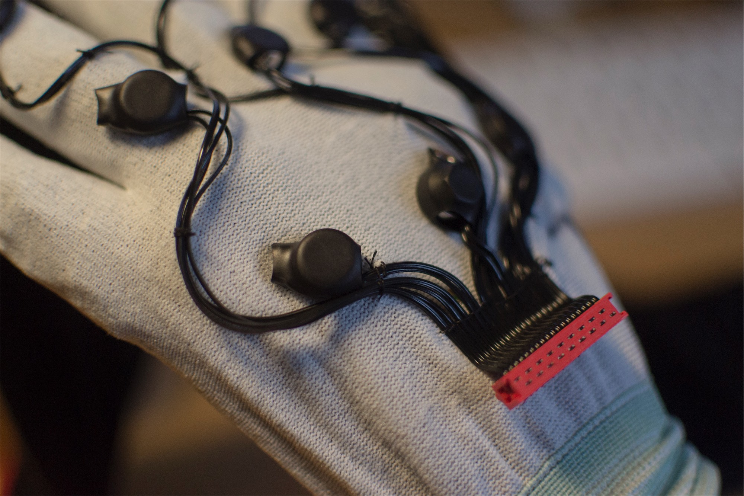
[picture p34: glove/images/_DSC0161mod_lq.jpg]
Close up of the glove affixed on the carboard hand. Now with finished seams fixing the cables.
|  |
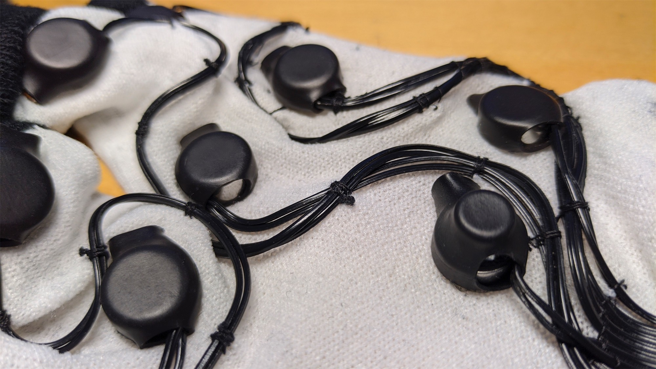
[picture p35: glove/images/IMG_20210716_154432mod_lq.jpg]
Close up of a seam around a cable only
|                                               |

Now the already joined outer part of the glove could be put over the inner part and the glove was practically completed.

| Steps of Implementation                                                                                                                                                                                                                                                                                                                                                    |
|:--------------------------------------------------------------------------------------------------------------------------------------------------------------------------------------------------------------------------------------------------------------------------------------------------------------------------------------------------------------------------:|
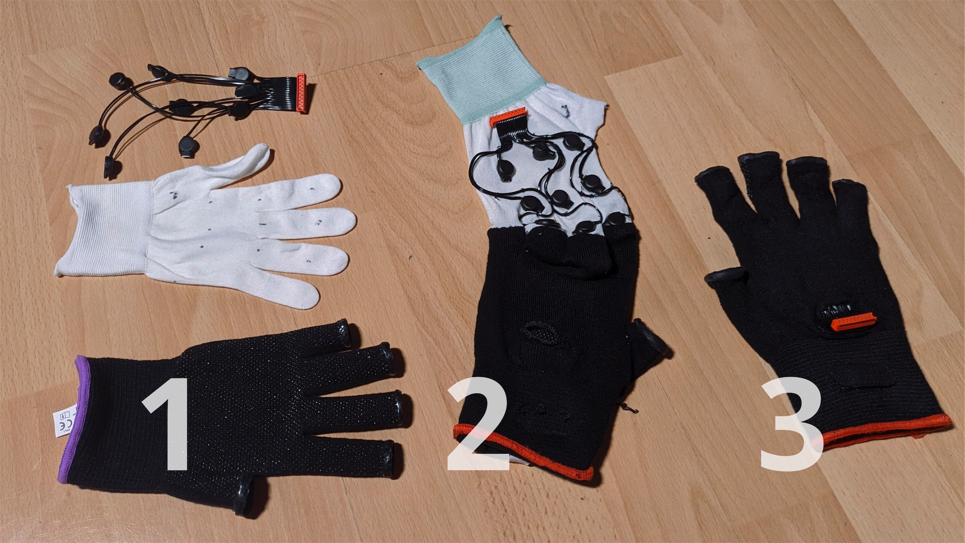
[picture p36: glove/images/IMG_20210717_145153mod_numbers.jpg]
Three steps of implementation: First, the wiring, the inner and the outer glove layer spearated on the table. Second, these three components got sewed together. The wiring onto the inner glove and the fingers of the inner with the outer layer. Third shows the completed glove with the outer layer pu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
|  |
| 1) The three components separated. 2) Sewing of components completed. 3) Glove completed                                                                                                                                                                                                                                                                                   |

## 5. Adding Velcros and Finishing

Finally, I added some Velcro: firstly, to attach the "Unfolding Space Carrier Board" to the glove; secondly, to connect the inner and outer layers at the wrist without sewing them together, so that you can open them in case of error.

| Sewing the Velcros                                                                        |
|:-----------------------------------------------------------------------------------------:|
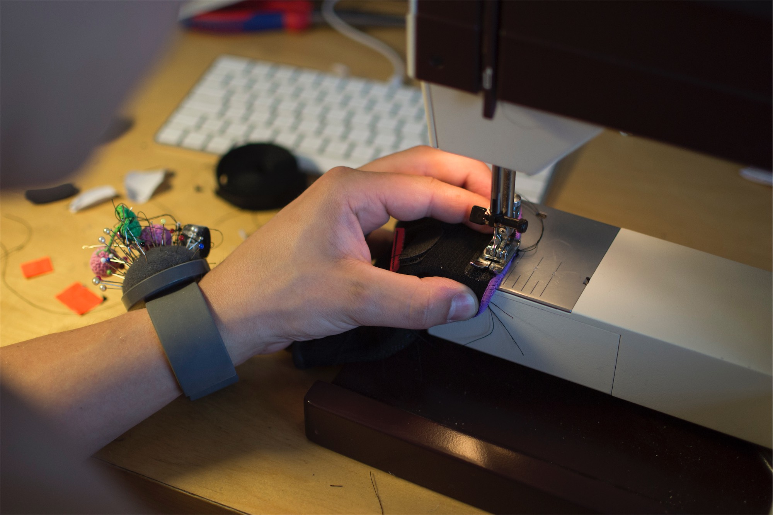
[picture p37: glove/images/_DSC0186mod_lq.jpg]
A sewing machine with someone sewing Velcro onto the glove.
|  |
| The sewing of the velcros was done with a sewing machine.                                 |

| Velcros for the Carrier Board                                                                                                                                                 |
|:-----------------------------------------------------------------------------------------------------------------------------------------------------------------------------:|
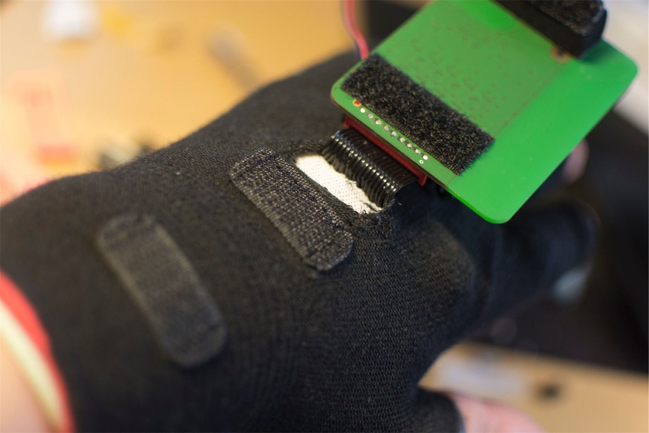
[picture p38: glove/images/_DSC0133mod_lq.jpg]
You can see the Velcro fasteners on the back of the glove and the Unfolding Space Carrier Board, which also has Velcros and folds away upwards.
|  |
| The velcros for fastening the carrier board and the slot where the ribbon cable exits the glove.                                                                              |

## Result

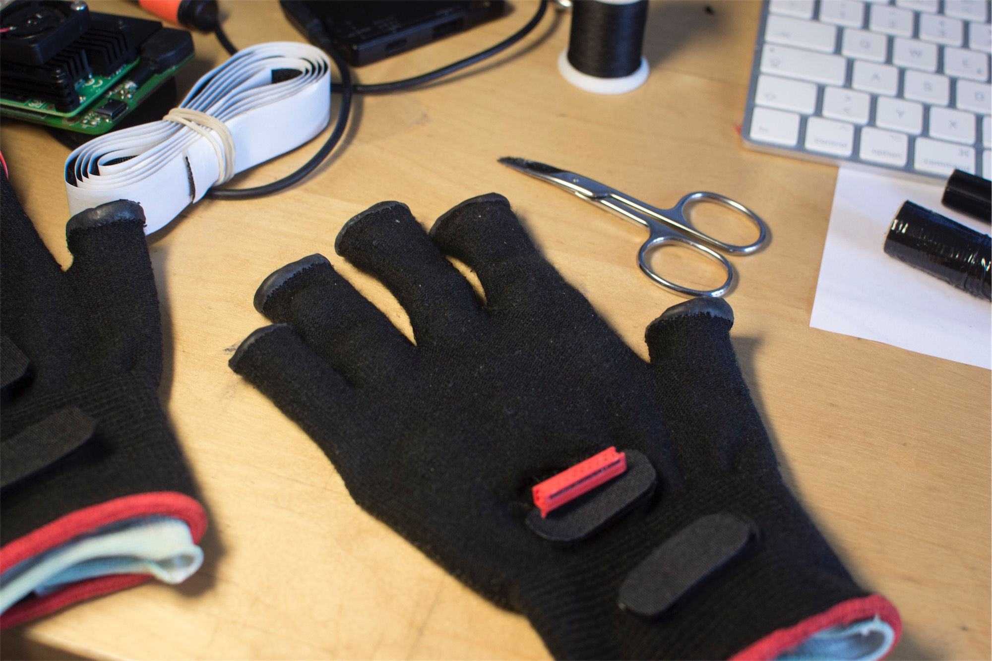
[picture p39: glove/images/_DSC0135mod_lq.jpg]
The glove on a table. Tools, a ruler, a scissor and the carrier board besides. The glove is now finished with velcros attached.
 

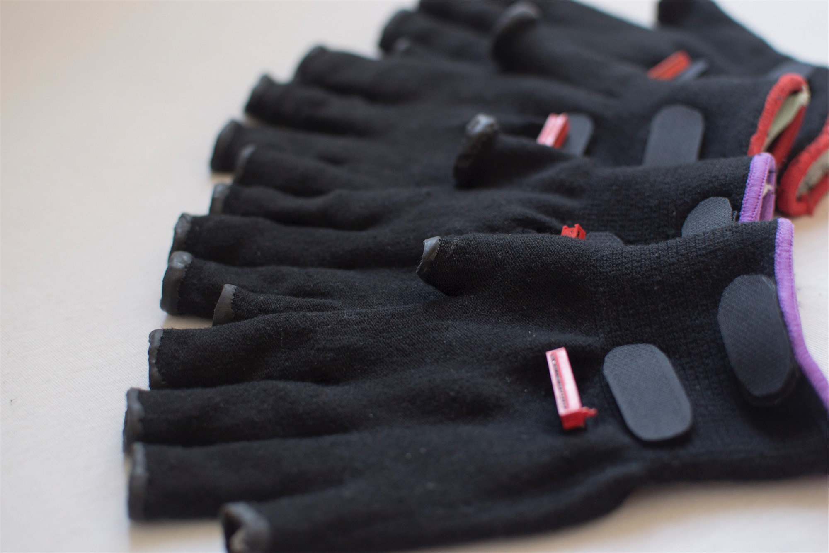
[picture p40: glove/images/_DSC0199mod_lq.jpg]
Four finished glove models next to each other.
 

**If you have any questions, feel free to mail me!**

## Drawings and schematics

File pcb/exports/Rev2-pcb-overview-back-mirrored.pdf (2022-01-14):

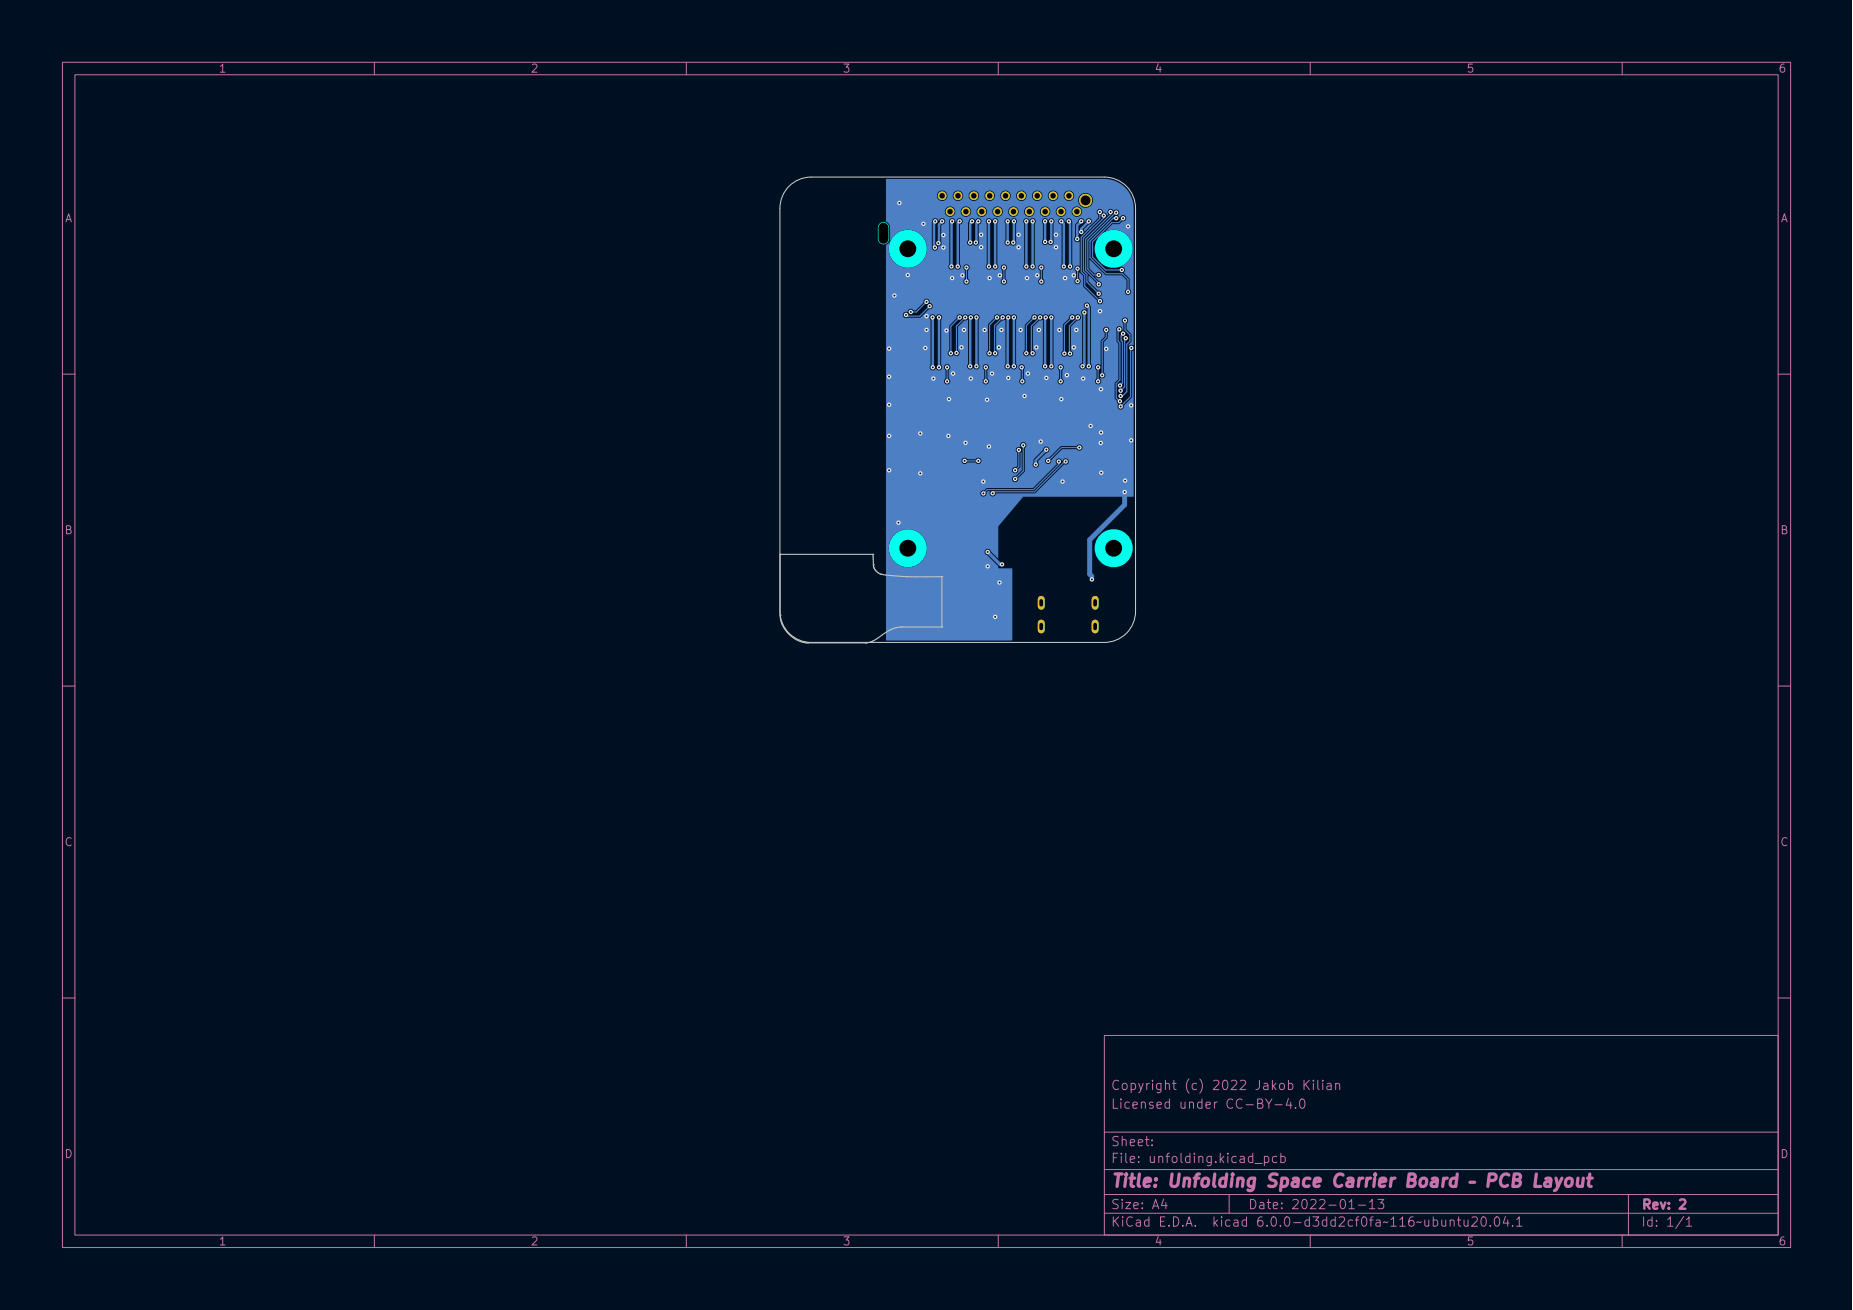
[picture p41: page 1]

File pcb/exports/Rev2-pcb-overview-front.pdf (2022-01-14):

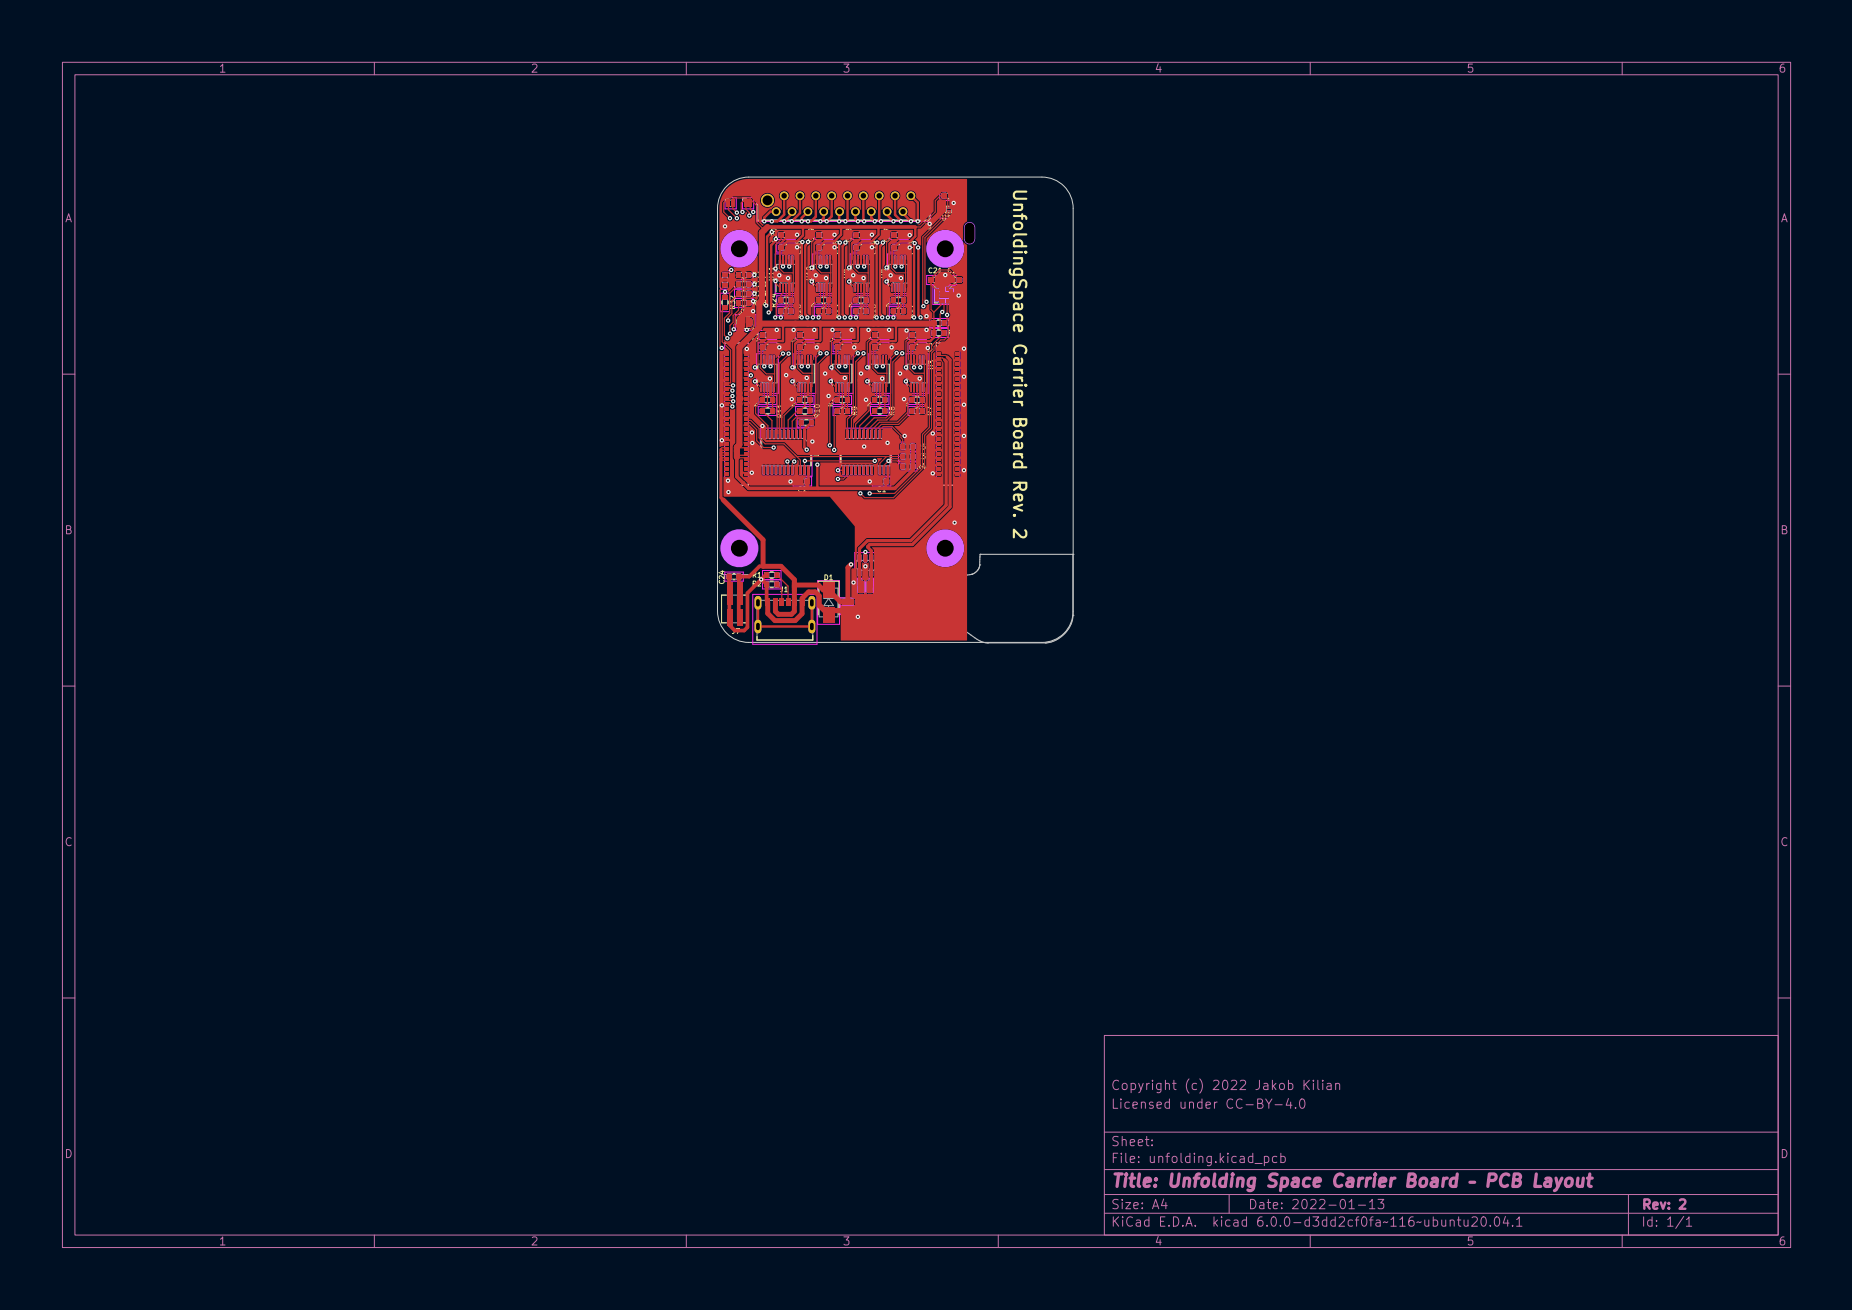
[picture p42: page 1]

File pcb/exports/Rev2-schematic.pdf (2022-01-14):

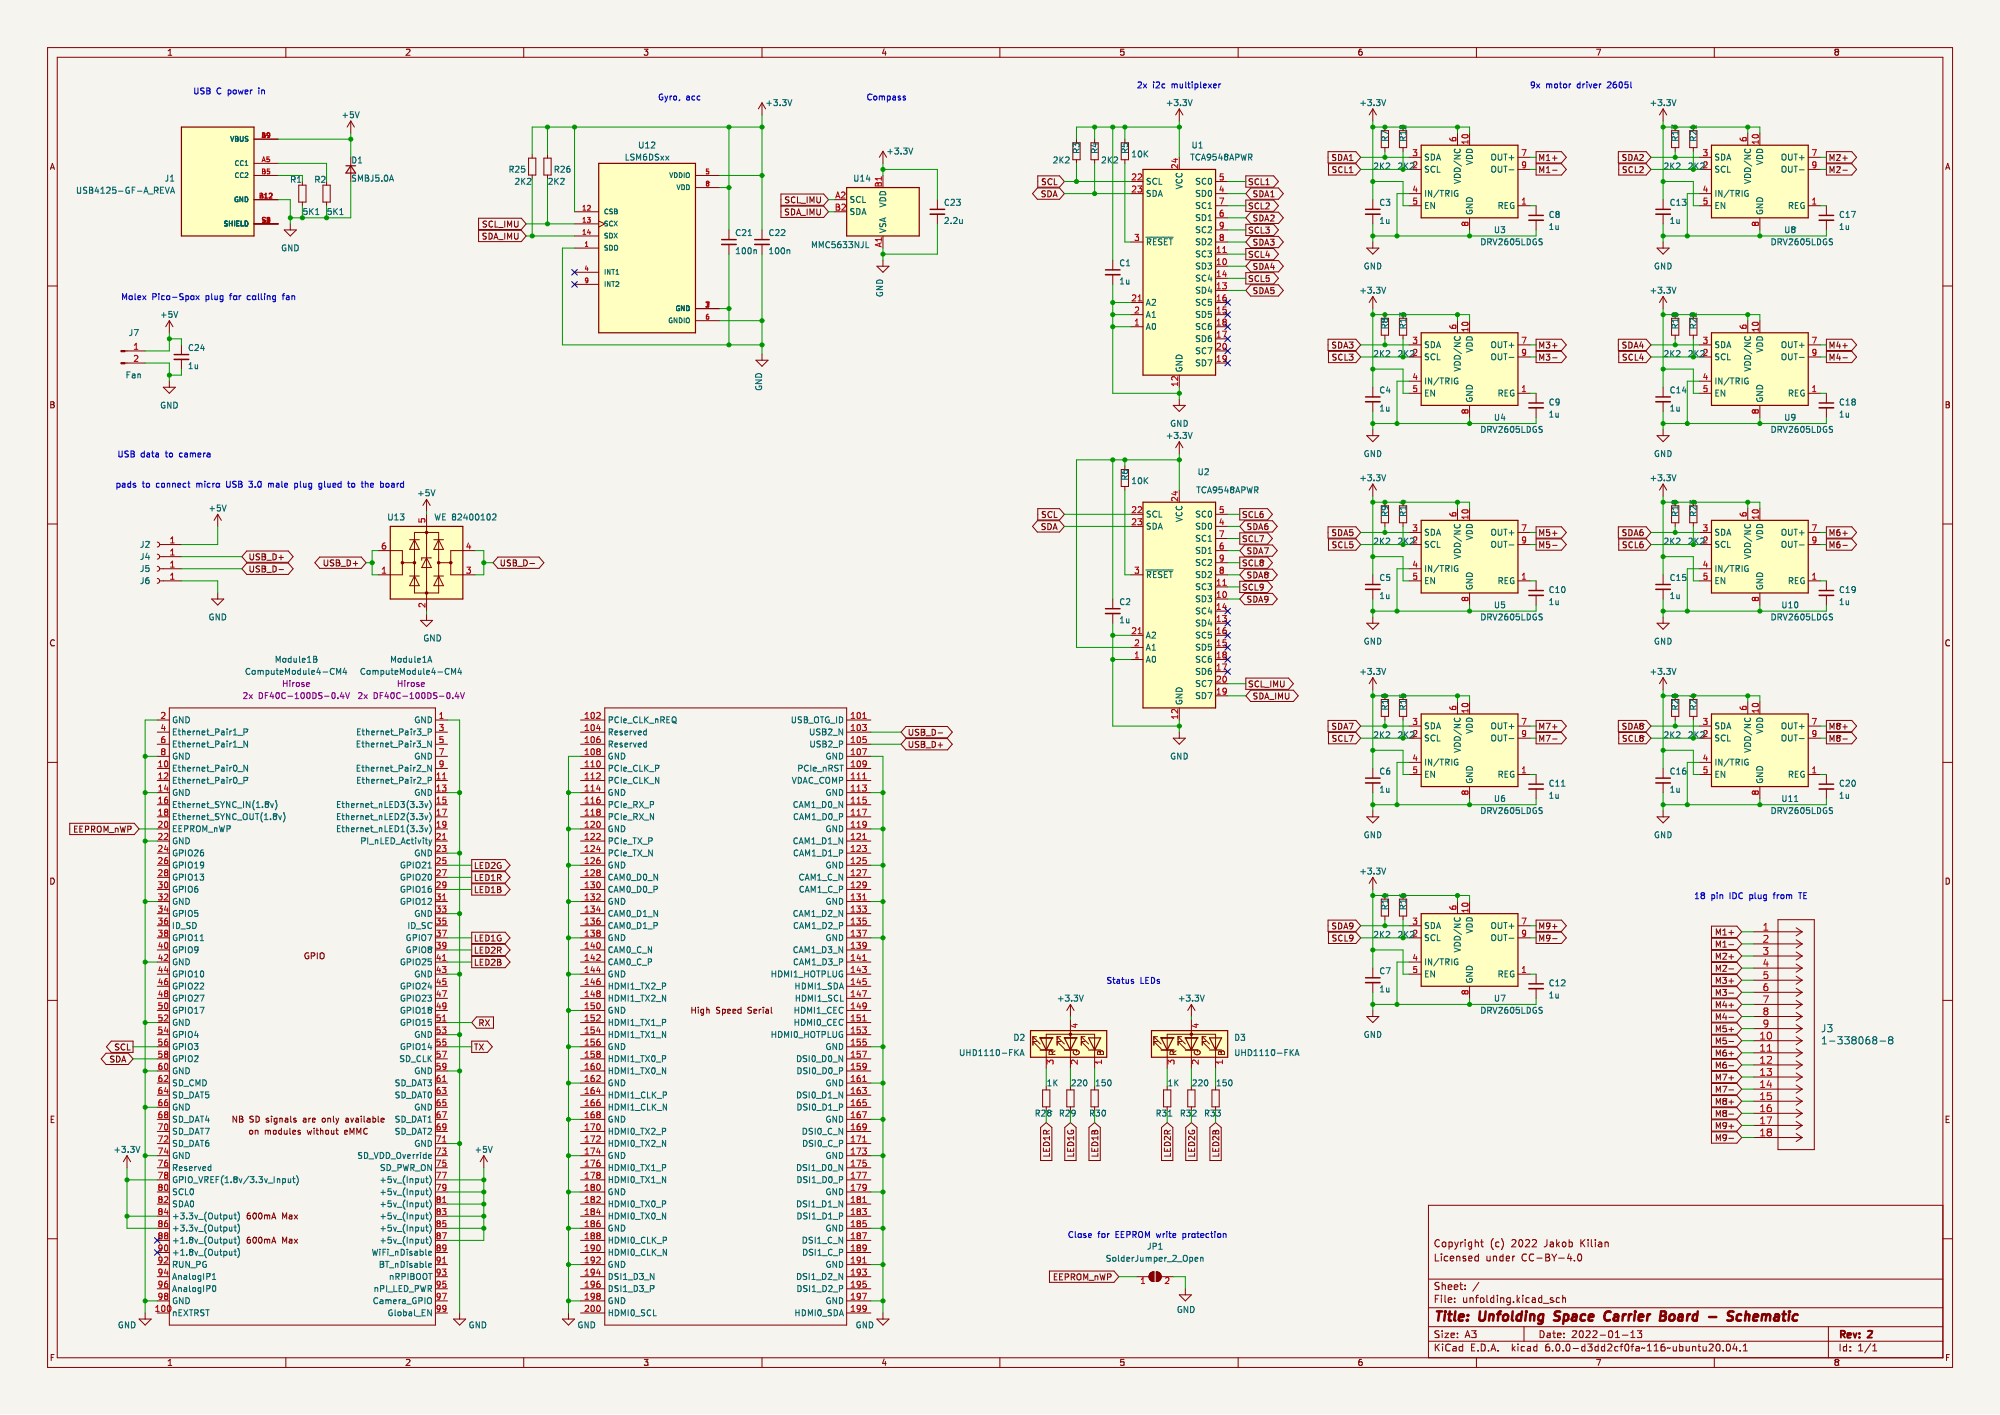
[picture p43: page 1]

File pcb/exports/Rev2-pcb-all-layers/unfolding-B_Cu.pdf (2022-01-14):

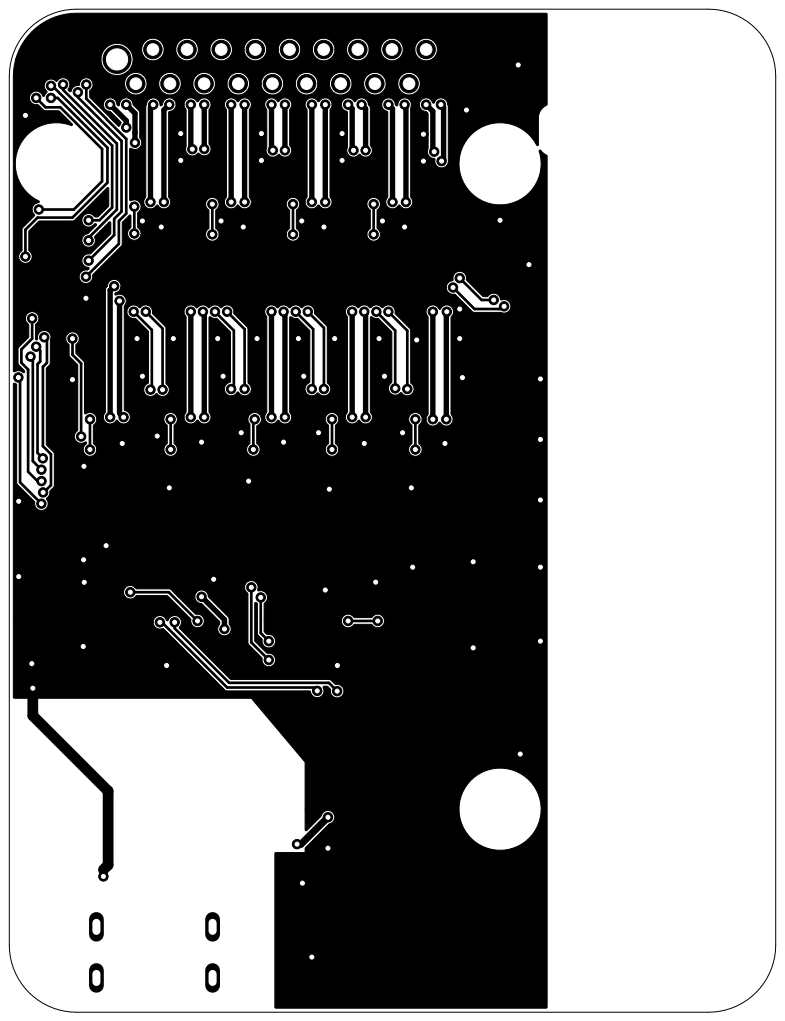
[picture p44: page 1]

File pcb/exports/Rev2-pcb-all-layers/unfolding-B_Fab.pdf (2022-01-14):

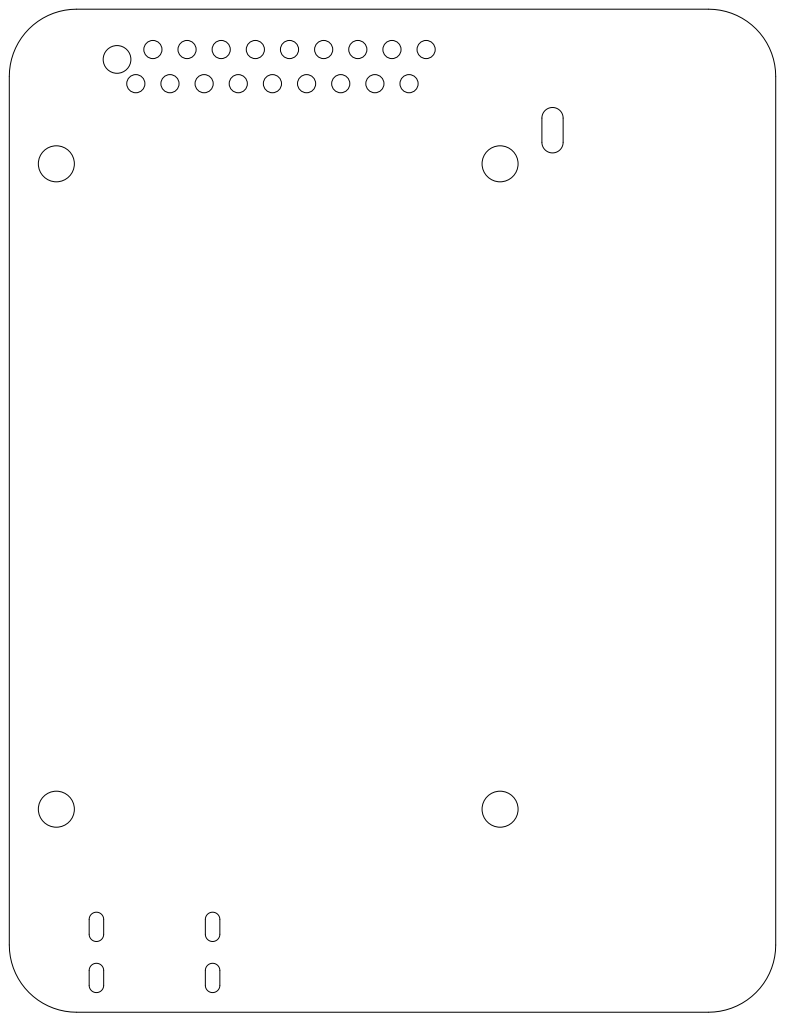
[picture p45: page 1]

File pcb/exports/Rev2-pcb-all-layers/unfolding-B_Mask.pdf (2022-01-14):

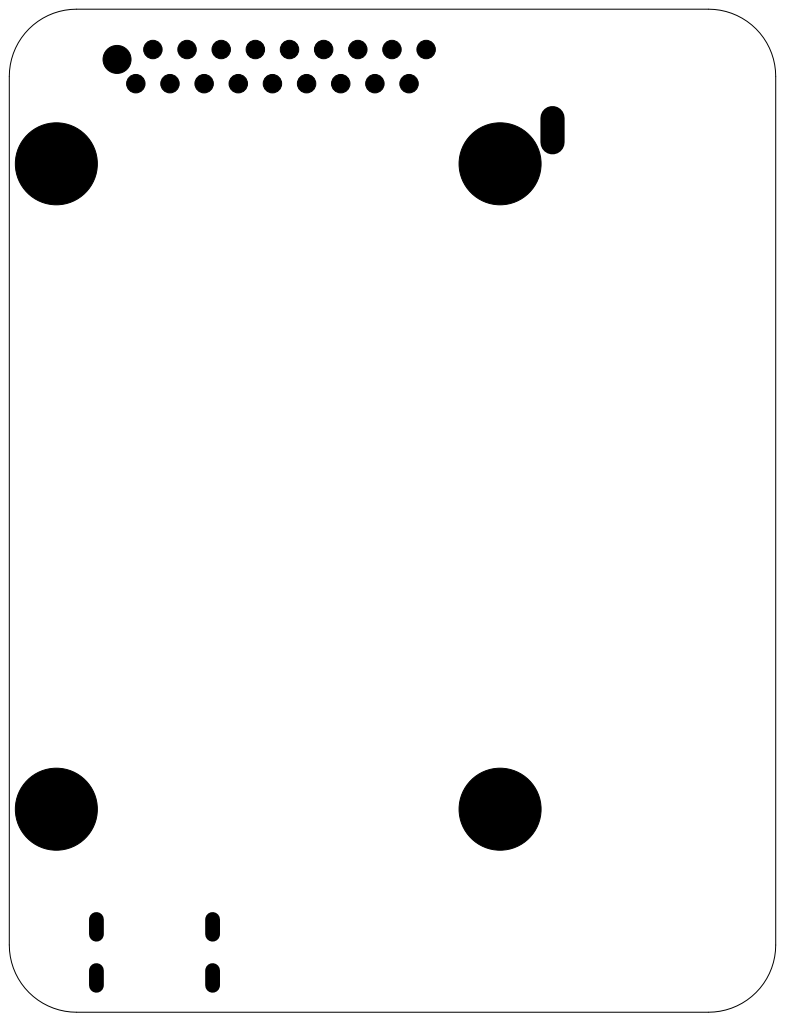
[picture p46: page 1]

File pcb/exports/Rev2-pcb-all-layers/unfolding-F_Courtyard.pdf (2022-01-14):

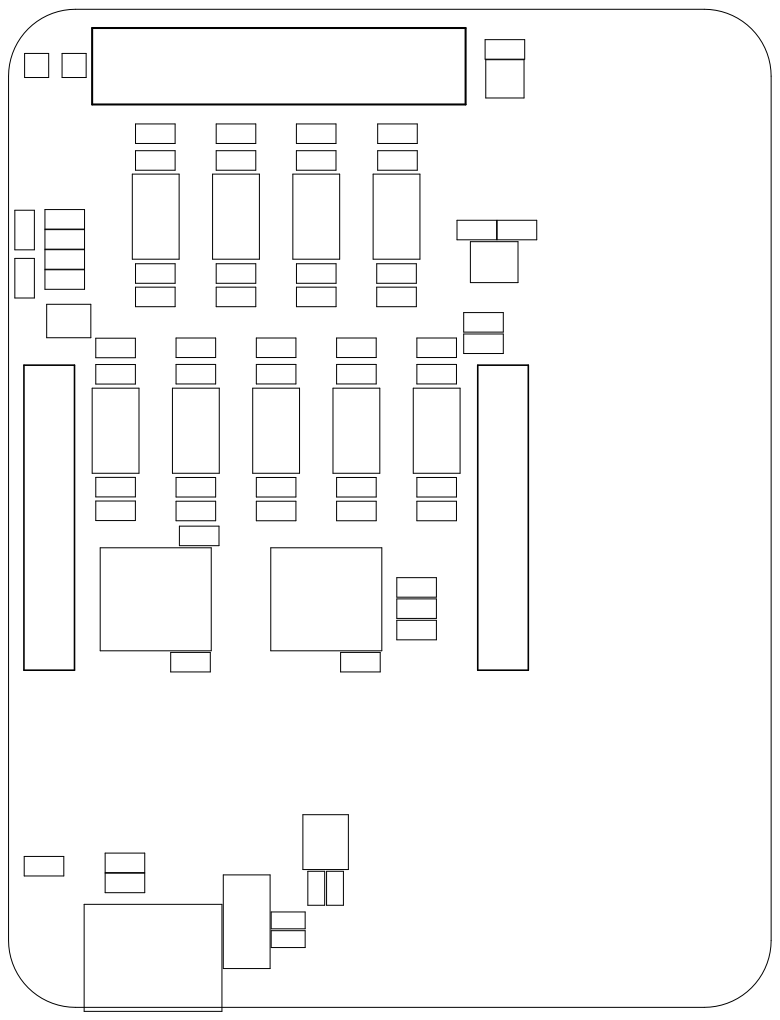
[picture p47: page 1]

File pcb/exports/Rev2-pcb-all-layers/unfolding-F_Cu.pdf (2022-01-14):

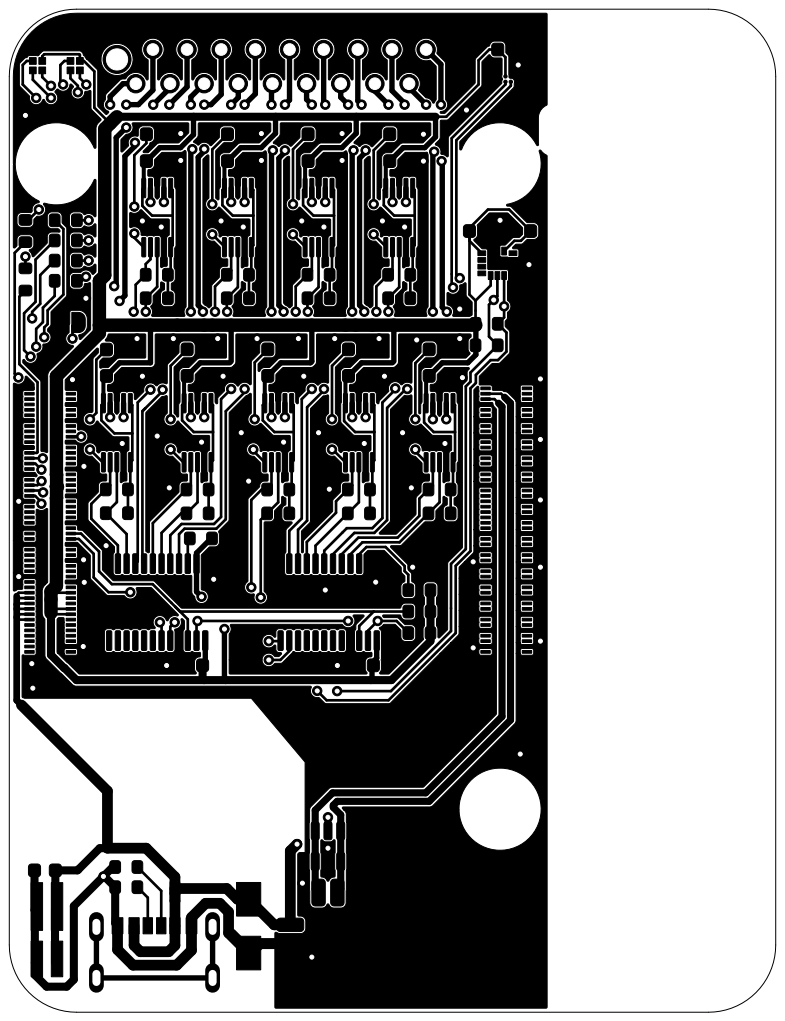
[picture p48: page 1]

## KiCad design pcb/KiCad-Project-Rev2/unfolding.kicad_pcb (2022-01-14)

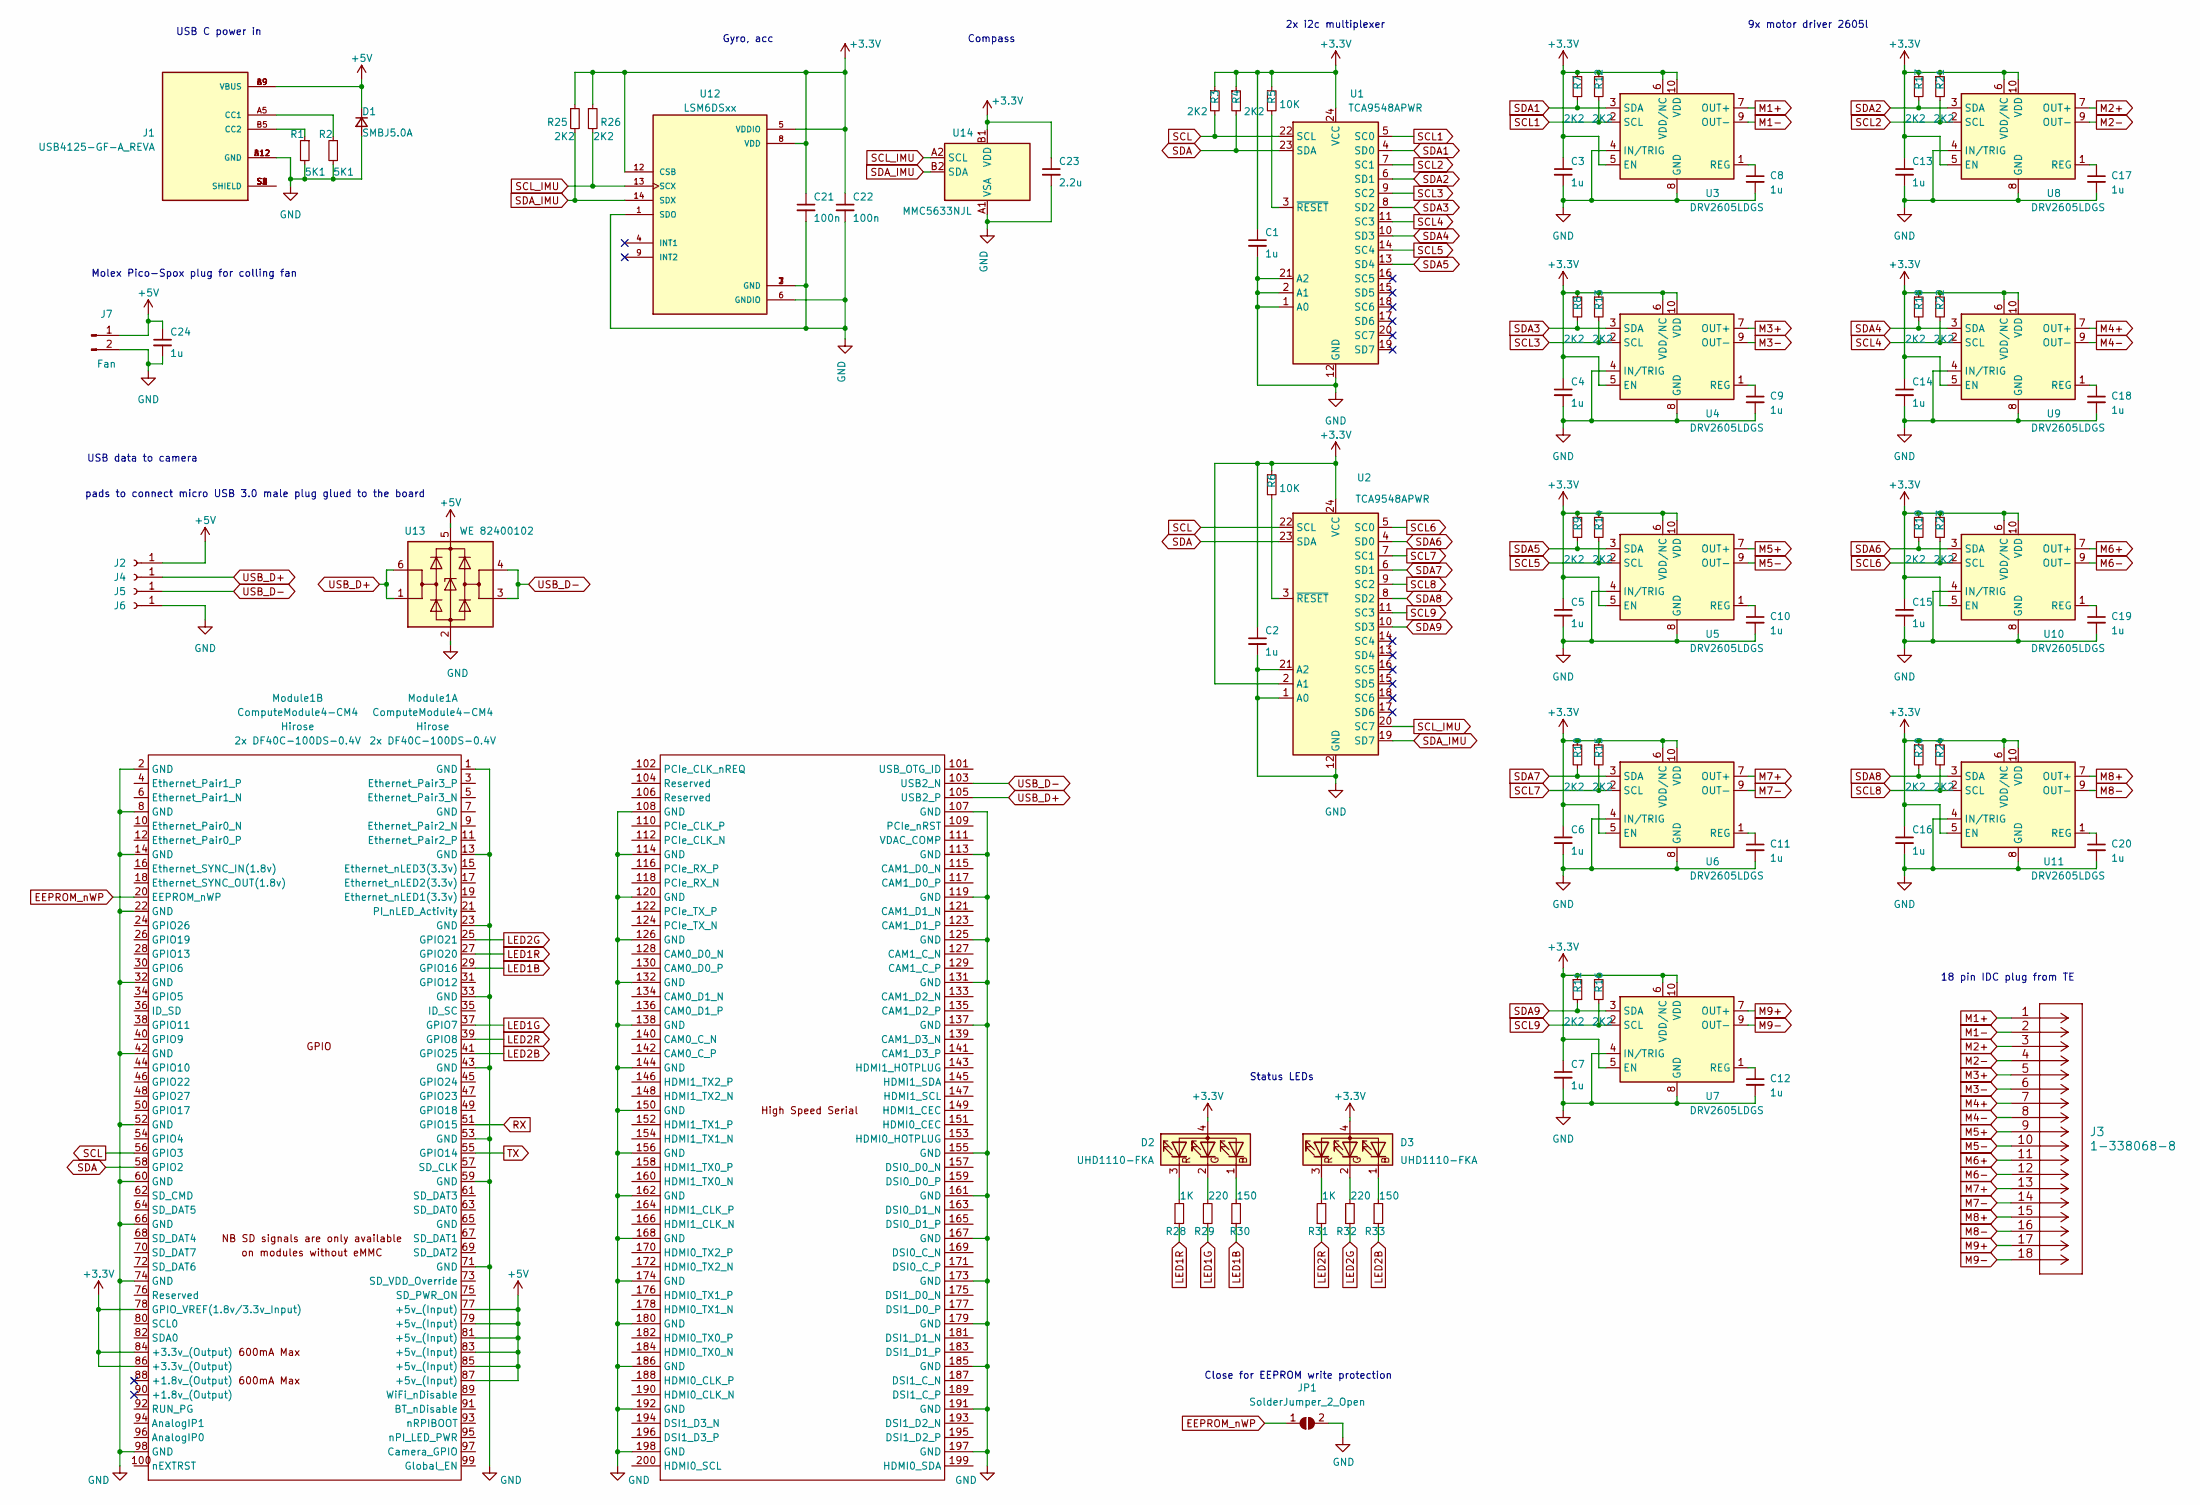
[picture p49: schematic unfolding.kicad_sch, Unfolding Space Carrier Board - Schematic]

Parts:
C1, C2, C3, C4, C5, C6, C7, C8, C9, C10, C11, C12, C13, C14, C15, C16, C17, C18, C19, C20, C24: 1u; C_0603_1608Metric
C21, C22: 100n; C_0603_1608Metric
C23: 2.2u; C_0603_1608Metric
D1: SMBJ5.0A; D_SMA
D2, D3: UHD1110-FKA
J1: USB4125-GF-A_REVA; GCT_USB4125-GF-A_REVA; PARTREV Rev A
J2, J4, J5, J6: Conn_01x01_Female; SolderWirePad_1x01_SMD_1x2mm
J3: 1-338068-8
J7: Fan; PICOspox-2-v
JP1: SolderJumper_2_Open; SolderJumper-2_P1.3mm_Open_RoundedPad1.0x1.5mm
Module1: ComputeModule4-CM4; Raspberry-Pi-4-Compute-Module
R1, R2: 5K1; R_0603_1608Metric
R3, R4, R7, R8, R9, R10, R11, R12, R13, R14, R15, R16, R17, R18, R19, R20, R21, R22, R23, R24, R25, R26: 2K2; R_0603_1608Metric
R5, R6: 10K; R_0603_1608Metric
R28, R31: 1K; R_0603_1608Metric
R29, R32: 220; R_0603_1608Metric
R30, R33: 150; R_0603_1608Metric
U1, U2: TCA9548APWR; TSSOP-24_4.4x7.8mm_P0.65mm
U3, U4, U5, U6, U7, U8, U9, U10, U11: DRV2605LDGS; VSSOP-10_3x3mm_P0.5mm
U12: LSM6DSxx; PQFN50P250X300X100-14N; PARTREV 1.2
U13: WE 82400102; SOT-23-6
U14: MMC5633NJL; WLP-4_0.86x0.86mm_P0.4mm

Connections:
+3V3: C1.1, C2.1, C3.1, C4.1, C5.1, C6.1, C7.1, C13.1, C14.1, C15.1, C16.1, C21.1, C22.1, C23.1, D2.4 (A), D3.4 (A), Module1.78 (GPIO_VREF(1.8v/3.3v_Input)), Module1.84 (+3.3v_(Output)), Module1.86 (+3.3v_(Output)), R3.1, R4.1, R5.1, R6.1, R7.1, R8.1, R9.1, R10.1, R11.1, R12.1, R13.1, R14.1, R15.1, R16.1, R17.1, R18.1, R19.1, R20.1, R21.1, R22.1, R23.1, R24.1, R25.1, R26.1, U1.24 (VCC), U2.2 (A1), U2.24 (VCC), U3.5 (EN), U3.6 (VDD/NC), U3.10 (VDD), U4.5 (EN), U4.6 (VDD/NC), U4.10 (VDD), U5.5 (EN), U5.6 (VDD/NC), U5.10 (VDD), U6.5 (EN), U6.6 (VDD/NC), U6.10 (VDD), U7.5 (EN), U7.6 (VDD/NC), U7.10 (VDD), U8.5 (EN), U8.6 (VDD/NC), U8.10 (VDD), U9.5 (EN), U9.6 (VDD/NC), U9.10 (VDD), U10.5 (EN), U10.6 (VDD/NC), U10.10 (VDD), U11.5 (EN), U11.6 (VDD/NC), U11.10 (VDD), U12.5 (VDDIO), U12.8 (VDD), U12.12 (CSB), U14.B1 (VDD)
+5V: C24.1, D1.1 (K), J1.A9 (VBUS), J1.B9 (VBUS), J2.1, J7.1, Module1.77 (+5v_(Input)), Module1.79 (+5v_(Input)), Module1.81 (+5v_(Input)), Module1.83 (+5v_(Input)), Module1.85 (+5v_(Input)), Module1.87 (+5v_(Input)), U13.5 (VBUS)
EEPROM_nWP: JP1.1 (A), Module1.20 (EEPROM_nWP)
GND: C1.2, C2.2, C3.2, C4.2, C5.2, C6.2, C7.2, C8.2, C9.2, C10.2, C11.2, C12.2, C13.2, C14.2, C15.2, C16.2, C17.2, C18.2, C19.2, C20.2, C21.2, C22.2, C23.2, C24.2, D1.2 (A), J1.A12 (GND), J1.B12 (GND), J6.1, J7.2, JP1.2 (B), Module1.1 (GND), Module1.2 (GND), Module1.8 (GND), Module1.13 (GND), Module1.14 (GND), Module1.22 (GND), Module1.23 (GND), Module1.32 (GND), Module1.33 (GND), Module1.42 (GND), Module1.43 (GND), Module1.52 (GND), Module1.53 (GND), Module1.59 (GND), Module1.60 (GND), Module1.66 (GND), Module1.71 (GND), Module1.74 (GND), Module1.98 (GND), Module1.107 (GND), Module1.108 (GND), Module1.113 (GND), Module1.114 (GND), Module1.119 (GND), Module1.120 (GND), Module1.125 (GND), Module1.126 (GND), Module1.131 (GND), Module1.132 (GND), Module1.137 (GND), Module1.138 (GND), Module1.144 (GND), Module1.150 (GND), Module1.155 (GND), Module1.156 (GND), Module1.161 (GND), Module1.162 (GND), Module1.167 (GND), Module1.168 (GND), Module1.173 (GND), Module1.174 (GND), Module1.179 (GND), Module1.180 (GND), Module1.185 (GND), Module1.186 (GND), Module1.191 (GND), Module1.192 (GND), Module1.197 (GND), Module1.198 (GND), R1.2, R2.2, U1.1 (A0), U1.2 (A1), U1.12 (GND), U1.21 (A2), U2.1 (A0), U2.12 (GND), U2.21 (A2), U3.4 (IN/TRIG), U3.8 (GND), U4.4 (IN/TRIG), U4.8 (GND), U5.4 (IN/TRIG), U5.8 (GND), U6.4 (IN/TRIG), U6.8 (GND), U7.4 (IN/TRIG), U7.8 (GND), U8.4 (IN/TRIG), U8.8 (GND), U9.4 (IN/TRIG), U9.8 (GND), U10.4 (IN/TRIG), U10.8 (GND), U11.4 (IN/TRIG), U11.8 (GND), U12.1 (SDO), U12.2 (GND), U12.3 (GND), U12.6 (GNDIO), U12.7 (GND), U13.2 (GND), U14.A1 (VSA)
LED1B: Module1.29 (GPIO16), R30.1
LED1G: Module1.37 (GPIO7), R29.1
LED1R: Module1.27 (GPIO20), R28.1
LED2B: Module1.41 (GPIO25), R33.1
LED2G: Module1.25 (GPIO21), R32.1
LED2R: Module1.39 (GPIO8), R31.1
M1+: J3.1, U3.7 (OUT+)
M1-: J3.2, U3.9 (OUT-)
M2+: J3.3, U8.7 (OUT+)
M2-: J3.4, U8.9 (OUT-)
M3+: J3.5, U4.7 (OUT+)
M3-: J3.6, U4.9 (OUT-)
M4+: J3.7, U9.7 (OUT+)
M4-: J3.8, U9.9 (OUT-)
M5+: J3.9, U5.7 (OUT+)
M5-: J3.10, U5.9 (OUT-)
M6+: J3.11, U10.7 (OUT+)
M6-: J3.12, U10.9 (OUT-)
M7+: J3.13, U6.7 (OUT+)
M7-: J3.14, U6.9 (OUT-)
M8+: J3.15, U11.7 (OUT+)
M8-: J3.16, U11.9 (OUT-)
M9+: J3.17, U7.7 (OUT+)
M9-: J3.18, U7.9 (OUT-)
unnamed: C8.1, U3.1 (REG)
unnamed: C9.1, U4.1 (REG)
unnamed: C10.1, U5.1 (REG)
unnamed: C11.1, U6.1 (REG)
unnamed: C12.1, U7.1 (REG)
unnamed: C17.1, U8.1 (REG)
unnamed: C18.1, U9.1 (REG)
unnamed: C19.1, U10.1 (REG)
unnamed: C20.1, U11.1 (REG)
unnamed: D2.1 (BK), R30.2
unnamed: D2.2 (GK), R29.2
unnamed: D2.3 (RK), R28.2
unnamed: D3.1 (BK), R33.2
unnamed: D3.2 (GK), R32.2
unnamed: D3.3 (RK), R31.2
unnamed: J1.A5 (CC1), R2.1
unnamed: J1.B5 (CC2), R1.1
unnamed: J1.S1 (SHIELD), J1.S2 (SHIELD), J1.S3 (SHIELD), J1.S4 (SHIELD)
unnamed: R5.2, U1.3 (~RESET)
unnamed: R6.2, U2.3 (~RESET)
RX: Module1.51 (GPIO15)
SCL: Module1.56 (GPIO3), R3.2, U1.22 (SCL), U2.22 (SCL)
SCL1: R12.2, U1.5 (SC0), U3.2 (SCL)
SCL2: R21.2, U1.7 (SC1), U8.2 (SCL)
SCL3: R13.2, U1.9 (SC2), U4.2 (SCL)
SCL4: R22.2, U1.11 (SC3), U9.2 (SCL)
SCL5: R14.2, U1.14 (SC4), U5.2 (SCL)
SCL6: R23.2, U2.5 (SC0), U10.2 (SCL)
SCL7: R15.2, U2.7 (SC1), U6.2 (SCL)
SCL8: R24.2, U2.9 (SC2), U11.2 (SCL)
SCL9: R16.2, U2.11 (SC3), U7.2 (SCL)
SCL_IMU: R26.2, U2.20 (SC7), U12.13 (SCX), U14.A2 (SCL)
SDA: Module1.58 (GPIO2), R4.2, U1.23 (SDA), U2.23 (SDA)
SDA1: R7.2, U1.4 (SD0), U3.3 (SDA)
SDA2: R17.2, U1.6 (SD1), U8.3 (SDA)
SDA3: R8.2, U1.8 (SD2), U4.3 (SDA)
SDA4: R18.2, U1.10 (SD3), U9.3 (SDA)
SDA5: R9.2, U1.13 (SD4), U5.3 (SDA)
SDA6: R19.2, U2.4 (SD0), U10.3 (SDA)
SDA7: R10.2, U2.6 (SD1), U6.3 (SDA)
SDA8: R20.2, U2.8 (SD2), U11.3 (SDA)
SDA9: R11.2, U2.10 (SD3), U7.3 (SDA)
SDA_IMU: R25.2, U2.19 (SD7), U12.14 (SDX), U14.B2 (SDA)
TX: Module1.55 (GPIO14)
USB_D+: J4.1, Module1.105 (USB2_P), U13.1 (I/O1), U13.6 (I/O1)
USB_D-: J5.1, Module1.103 (USB2_N), U13.3 (I/O2), U13.4 (I/O2)

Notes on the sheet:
Molex Pico-Spox plug for colling fan
Status LEDs
pads to connect micro USB 3.0 male plug glued to the board
Gyro, acc
USB C power in
Close for EEPROM write protection
USB data to camera
9x motor driver 2605l
2x i2c multiplexer
Compass
18 pin IDC plug from TE

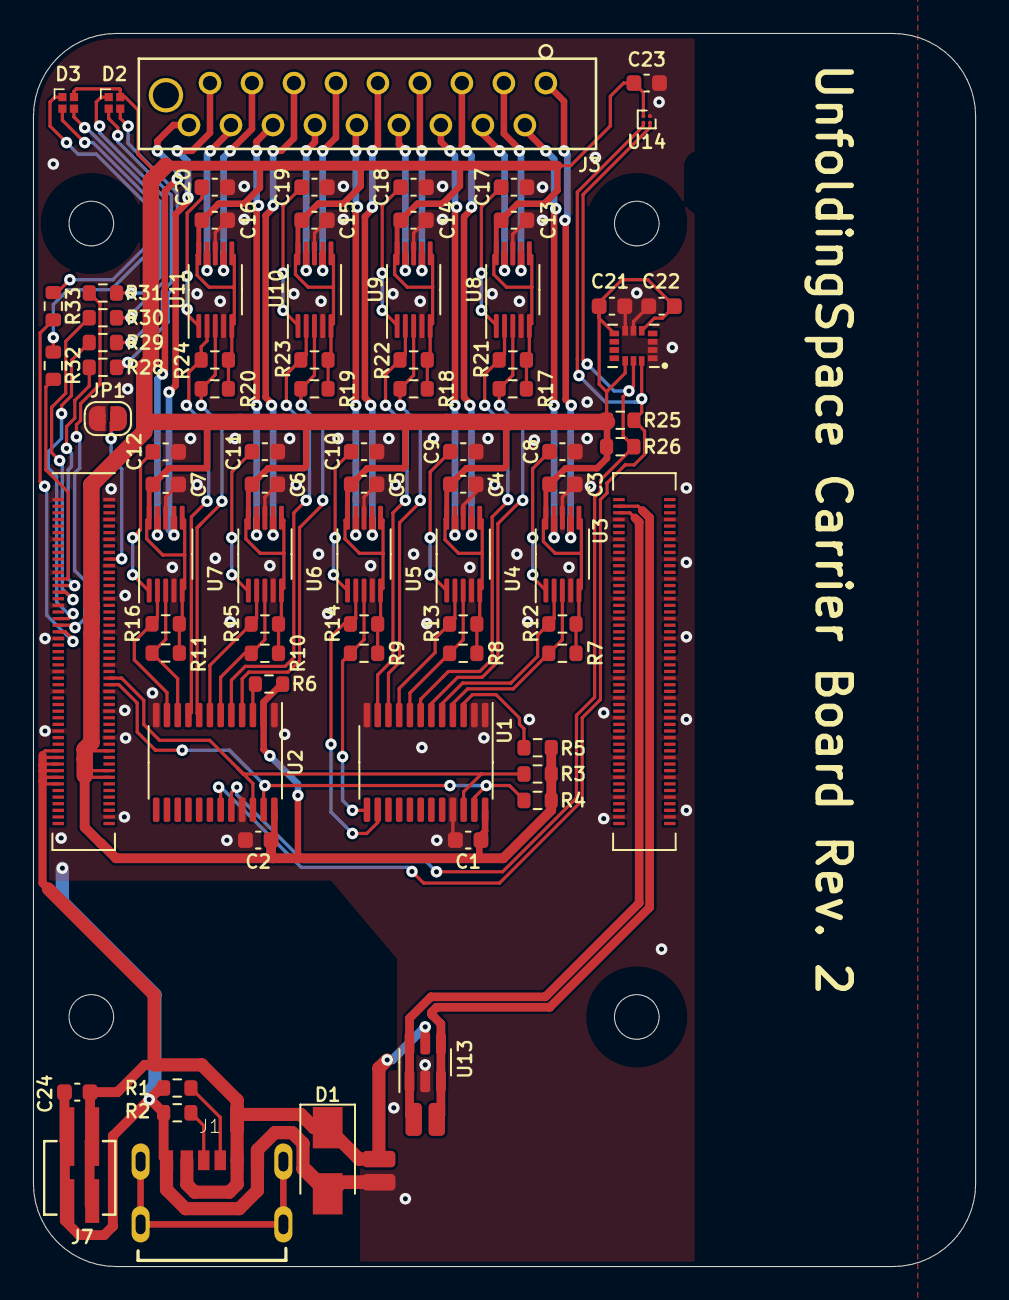
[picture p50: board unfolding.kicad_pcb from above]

Board: 2 copper layers, 57.0 x 74.6 mm, 83 parts (0 on the bottom side), 72 nets.

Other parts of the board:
ToFCam-Stecker: ToFCam-Stecker; SteckerMicro-USB30-gewinkelt

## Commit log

2021-03-30 First version, rudimentary schematics and layout
    [unfolding.kicad_pcb, unfolding.kicad_sch]
2021-04-02 Change Folder Structure. Move PCB files to "carrier-pcb"
    [unfolding.kicad_pcb, unfolding.kicad_sch]
2021-04-02 Add usb plug. Add fusion archive. Delete GrabCAD file – identical to raspi.org step file
    [startech-micro-usb-stecker.step]
2021-04-12 Add camera clamp and heatsink
2021-04-19 Add 3rd_party_libs folder and place footrpints and symbols. Place bmx160 and TE IDC connector. Add route_try file to try out routing.
    [unfolding.kicad_sch, unfolding_route_try.kicad_pcb]
2021-04-21 Route everything in route_try file
    [unfolding_route_try.kicad_pcb, unfolding_route_try.kicad_sch]
2021-04-23 New routing
    [unfolding_route_try.kicad_pcb, unfolding_route_try.kicad_sch]
2021-04-23 finish new routing with diff pair. export stp file.
    [c-1-215083-8-u-3d.stp, unfolding_route_try.kicad_pcb, unfolding_route_try.kicad_sch]
2021-04-26 reroute usb traces. make motor traces thicker. small changes
    [unfolding_route_try.kicad_pcb]
2021-04-26 add roundings, add BOM
    [unfolding_route_try.csv, unfolding_route_try.kicad_pcb]
2021-04-29 change diode footprint
    [unfolding_route_try.kicad_pcb, unfolding_route_try.kicad_sch]
2021-04-30 change ESD protection. change usb plug. reroute
    [UJC-HP-3-SMT-TR.step, USBLC6-2SC6.step, unfolding_route_try.kicad_pcb, unfolding_route_try.kicad_sch]
2021-05-23 Bestellte Version
    [unfolding_route_try.kicad_pcb]
2021-06-28 Added compass, added LEDs, changed USB TVS diode, fixed power TVS diode direction, moved accelerometer, misc minor improvements
    [unfolding_route_try.kicad_pcb, unfolding_route_try.kicad_sch]
2021-06-28 Added Pico-SPOX connector for 5V fan
    [unfolding_route_try.kicad_pcb, unfolding_route_try.kicad_sch]
2021-06-29 Add milling for camera fixation rubber band. Add silkscreen text "UnfoldingSpace Carrier Board Rev. 2"
    [unfolding_route_try.kicad_pcb]
2021-06-29 removed more backups and renamed files. USE MORE BRANCHES, DONT RENAME
    [unfolding.csv, unfolding.kicad_pcb, unfolding.kicad_sch, unfolding_route_try.kicad_pcb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]
2021-06-29 Changed RGB LED footprints
    [unfolding.kicad_pcb, unfolding.kicad_sch]
2021-06-29 Re-add non plated sot for rubber band for fixation of camera
    [unfolding.kicad_pcb]
2021-06-29 edit slot to min width of 1,6mm of aisler.net
    [unfolding.kicad_pcb]
2021-06-30 Lock Slot from last commit
    [unfolding.kicad_pcb]
2021-07-04 Add general docs folder (also for parts that are not on the pcb). Add chips and parts that are going to be used in rev 2 (v0.2)
2022-01-14 Restructure directories. New KiCad Verison + File. License notes. Add BOMs. Start documenting pcb
    [UJC-HP-3-SMT-TR.step, USBLC6-2SC6.step, bom-overall.csv, bom-pcb.csv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]
2022-01-14 Update Glove instructions
    [bom-glove.csv]
2022-01-14 update main readme and bom
    [bom-overall.csv]
2022-01-14 Update readme links. Move pcb image to /pcb. Update plug.step
    [startech-plug.step]
2022-01-14 Edit all BOMs - put links behind price
    [bom-glove.csv, bom-overall.csv, bom-pcb.csv]

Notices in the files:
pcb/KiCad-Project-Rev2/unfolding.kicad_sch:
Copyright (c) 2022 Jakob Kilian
